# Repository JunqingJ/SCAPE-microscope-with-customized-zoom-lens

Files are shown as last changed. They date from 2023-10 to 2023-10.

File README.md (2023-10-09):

# SCAPE-microscope-with-customized-zoom-lens
Detailed guideline containing both hardware and software to reproduce the SCAPE microscope with home-built zoom lens. Compare with other variations of OPM systems, SCAPE utilizes a galvo mirror for 3D imaging, making the acquisition much faster and drifting-free. Combining it with a home-built zoom lens, the new systems further extends the imaging capabilities to "any immersion medium" which no longer been constrained by the primary objective lens chosen. Such feature opens up much wider potential applications of SCAPE microscope and making the imaging of tissue-
cleared samples possible. 

The overall diagram of the microscope is shown below:



This project intends to offer those very beginner who barely had any optics background a not-so-intimidating starting point. Contents in this repository are mostly practical/hands-on oriented and keywords of theoretical concepts are provided.

Contact: chris.moraes@mcgill.ca or junqing.jiang@mail.mcgill.ca

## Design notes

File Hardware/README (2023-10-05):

List of drivers need to be downloaded:
* In case listed drivers are no longer available from the supplier, please contact chris.moraes@mcgill.ca for a copy
** Drivers that needs to be purchased separately are not included here (AndorSDK3, AndorSDK3 for MATLAB, Bitflow SDK 6.40)

-Laser: CoboltMonitor-6.1.0.0 (https://hubner-photonics.com/downloads/)

-Zoom lens linear stage: Kinesis 1.14.41 (https://www.thorlabs.com/software_pages/ViewSoftwarePage.cfm?Code=Motion_Control&viewtab=0)

-Bright field camera: ThorCam 	3.7.0 (https://www.thorlabs.com/software_pages/viewsoftwarepage.cfm?code=ThorCam)

-Sample stage: USB 4d stage 2.4 (https://picardindustries.com/other/software-downloads/)

-NI DAQ 6009 for galvo mirror: DAQmx

Steps to setup Andor Zyla 4.2+ in MicroManager (V2.0.0):

-Make sure BitFlow and properly installed 

-Open a new configuration and select Devices/Hardware Configuration Wizard/Create new configuration 

-Change the listing into ‘List by Type’, then go to camera/AndorSDK3: SDK3 Device Adaptor for sCMOS camera 

-Click OK, click next, leave everything by default. Don't forget to save the configuration

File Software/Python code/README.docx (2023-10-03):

Python version: 3.8.8 (Anaconda)

Complier: Spyder

Library & Dependency: No extra dependencies need to be downloaded. But make sure both “thorlabs_DDS050.py” and “thorlabs_DDS100.py” are in the same pathway as your main code

Extra: go to Device Manager, find Thorlabs 'APT USB device' (under USB controllers) and on the 'advanced' tab select the 'load VCP' check box to enable COM port

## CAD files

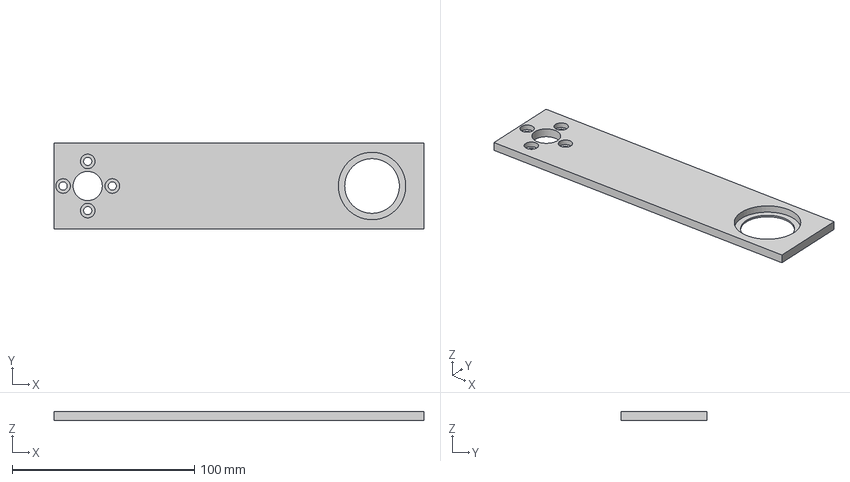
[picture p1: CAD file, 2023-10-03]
Hardware/Machined items/Picard sample arm.stp
203.0 x 47.0 x 5.00 mm

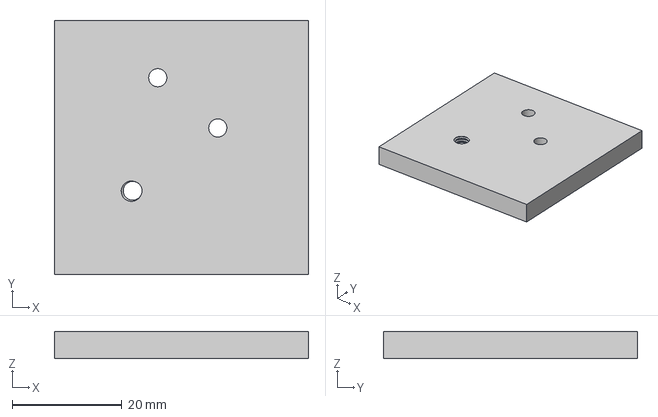
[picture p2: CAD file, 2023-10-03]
Hardware/Machined items/galvo center adaptor.stp
46.2 x 46.2 x 5.00 mm

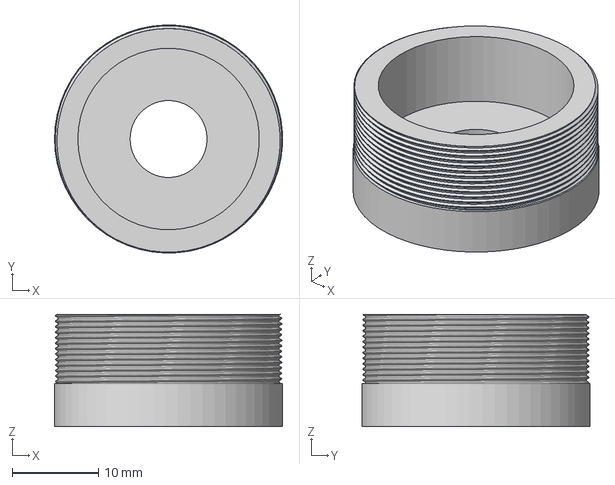
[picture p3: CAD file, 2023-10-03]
Hardware/Machined items/Powell lens.stp
26.4 x 26.4 x 13.0 mm

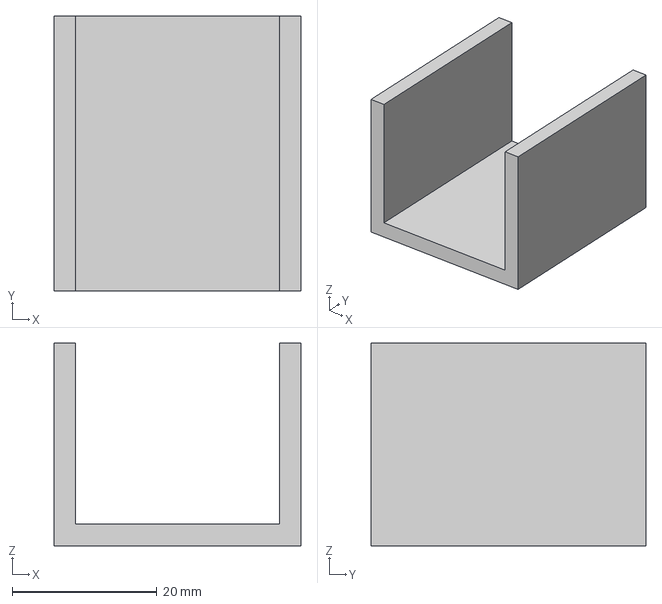
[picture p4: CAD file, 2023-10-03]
Hardware/Machined items/zoom lens spacer2.stp
34.1 x 38.0 x 28.0 mm

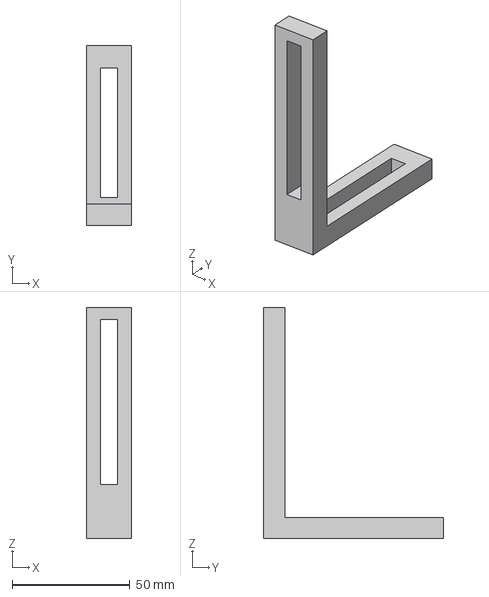
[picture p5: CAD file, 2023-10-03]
Hardware/Machined items/zoom lens angled bracket.stp
19.0 x 76.2 x 97.9 mm

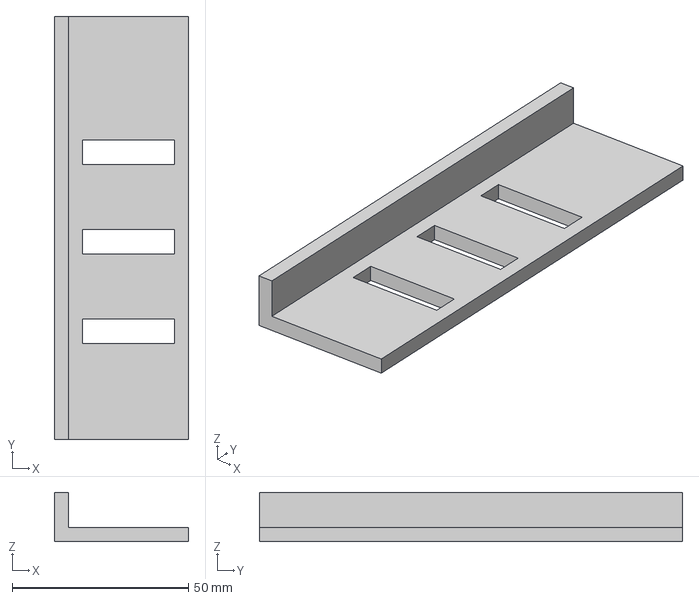
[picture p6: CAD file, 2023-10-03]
Hardware/Machined items/zoom lens guiding rail.stp
38.0 x 120.0 x 14.0 mm

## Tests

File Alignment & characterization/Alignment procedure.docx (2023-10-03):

Part I: Setting up the reference

1. Use a ruler to check the height of excitation laser beam
2. Setup a collimated low power green reference laser at one end of the optical table using Polaris mount. Make sure the center of the beam matches the height of excitation laser
3. Using at least 2 Iris along the beam path to make sure it is parallel in all 3 axes
4. Setup the manual rail at the desired position, leave 3 stages on it. Mount an Iris on the middle stage
5. Position the middle stage so it’s located at the center of reference laser. Replace the Iris with turning mirror and position it until it’s perfect 90 degree
6. Mount the galvo mirror at the end of manual rail. Position the height and rotation angle so the laser hits its center, and the angle is at perfect 90 degree
7. Confirm the height of reference beam at far away position
8. Setup O1 and O2 with their respective tube lens using cage system (see video on how to setup O1 with its cage system so it can be swapped in and out)
9. Input a secondary reference laser from the front end of objective lens. Adjust the position of tube lens until the output beam is collimated. These 2 cage systems can be set aside for later usage

Part II: Fluorescent light pathway until zoom lens

1. Setup the 70mm lens onto the 3rd stage on the rail and position it until laser remains on its reference pathway
2. Adjust the position of the stage until the laser is focused onto the galvo mirror. May need protection eyeglass for more accurate inspection
3. Setup a 50mm lens (or shorter focal distance) before the turning-mirror using a small cage system. Make sure the lens is mounted within a lens tube so it can be screwed in/out easily
4. Adjust the position of the lens so the laser remians on its reference pathway
5. Adjust the position of 50mm lens within the cage until the output laser after galvo is collimated. Then unscrew the lens tube
6. Setup the 88.9mm lens after galvo using a small cage system, adjust the position until the laser remains on its reference pathway
7. Adjust the position of 88.9mm lens within the cage until the output laser is collimated

Part III: Zoom lens: (find details in https://amsikking.github.io/any_immersion_remote_refocus_microscopy/appendix.html#zoom_lens)

Note: May need to machine several right-angle brackets that matches the desired height, guiding rail (check the video) as well as spacers

1. Setup all 3 P, N, P lens and position each linear stage on the plate at its desired position
2. Mount the plate onto the main optical table 2 holes after the 88.9mm lens
3. Place an Iris in between the plate and 88.9mm lens and another Iris far away along the reference laser pathway
4. Run the python code to set the stage at “132.5mm” position
5. Setup the first positive lens group on stage 1, adjust until the laser beam passes the center of faraway Iris (2 axes plus 2 rotation).
6. Close the Iris at the back to its minimum and make sure the back reflection hits the center of Iris in the back. Be gentle when fixing the position as over tightening may affect the alignment
7. Setup the negative lens group on stage 2 following the procedure in step 5 and 6. The 50mm lens may need to be swapped in/out to maintain desired laser spot size at faraway position
8. Setup the second positive lens group on stage 3 following the procedure in step 5 and 6. Make sure the back reflection light is clean and centered at the back Iris
9. Gently loosen the negative lens tube, use the spacer to find the appropriate position with respect to positive lens on stage 3. While fixing the position of negative lens tube, the spacer should be lightly held by the 2 lens tubes. Falling may indicate the imperfect alignment
10. Gently loosen the positive lens tube on stage 1 and follow the procedure in step 9 to find its appropriate position
11. Set up the guiding rail by placing them tightly against the side of the plate. Swap in the 50mm lens
12. Unscrew the plate and move it along the guiding rail until the output beam is collimated. Remove the 50mm lens
13. Setup a diffuser lens (can be made by scratching glass slide using sandpaper) and a small black screen
14. Position the diffuser lens at the focal point of the zoom lens, run the python code that position the zoom lens within its designed range. The speckle pattern observed on black screen can be used as a qualitative check for alignment
15. Remove the diffuser lens and black screen

Part IV: Fluorescent light pathway until O2:

Note: depending on the choice of dichroic mirror and O2, relay lens pair may not be necessary. The exact focal distance of relay lens pair does not particularly matter as long as they produce 1:1 magnification

1. Setup the dichroic mirror right after the zoom lens and position it until the mirror produces a perfect 90 degree reflection
2. Set up another manual rail and put in the 60mm lens. Follow step 4 and 5 in Part II to align the 60mm lens
3. Swap in the 50mm lens and unscrew the O2 from its small cage system
4. Align the second 60mm lens in a cage system following step 4 and 5 in Part II
5. Screw back in the O2 and remove 50mm lens. Fine adjust the alignment of the small cage system

Part V: Tilted alignment between O2 & O3

Note: Following steps involves compromise due to limited working space, ideally the position of O2 is never moved once been fixed in Part IV

1. Use 2 holdfast to mark the position of the stage where O2 is mounted. Then move the stage backwards until enough space is created so that O2 & O3 can be placed face-to-face at 180 degrees
2. Mount O3 with a turning mirror and position it onto a manual z-stage. The entire setup is mounted altogether onto a separate small plate for easier maneuver
3. Place a cage compatible Iris after O3 and place O3 in front of O2
4. Roughly adjust its position until the light spot passes through the center of Iris
5. Fine adjust and fix the height using z-stage and leave all other axes roughly aligned. Move the O2 back to its marked position
6. Start tilting the O3 incrementally, move the plate around after each tilt until the laser spot passes through the center of Iris
7. Depending on the O2 & O3 used, a tilting angle between 40-50 degrees should be aimed. Circular laser spot will start to be clipped into an eclipse/olive as the tilting angle increases
8. After the desired angle is reached (by eyeball, no need to be precise), fine adjust the position of the plate until the output beam is collimated and centered at the Iris
9. Gently fix the position of the plate using holdfast and insert emission filter and another turning mirror to turn the beam upwards
10. Mount camera with the commercial zoom lens and mount them altogether vertically onto a large z-translation stage (see in video)
11. Position the large z-stage until the laser beam roughly hits the center of commercial zoom lens

Part VI: O1 and bright-field imaging system

1. Change the angle of removable turning mirror in Part I so the laser is pointed towards the direction where O1 should be (the turning mirror is set up using separable cube so the base will ensure the angle is fixed once the mirror is inserted)
2. Place the cage system containing O1 onto the stage and mount a cage compatible Iris
3. Position the cage system until the laser spot passes through the center of the Iris
4. Remove O1 from the cage system and insert a secondary reference laser
5. Remove turning mirror and leave that cube empty. Swap in a dichroic mirror that will reflect the reference laser
6. Use a shear plate to check the collimation of beam reflected from the dichroic, adjust the position of O1 cage system until the beam is collimated
7. Bring back the turning mirror and make sure the laser is directed to the bright-field setup
8. Replace 50mm lens with a 100mm lens and adjust its position following step 4 and 5 in Part II
9. Mount the bright-field camera with its camera lens using a cage system and place a cage compatible Iris in front
10. Adjust the position of camera until the laser passes through the center of the Iris. There is no need to maintain 2f condition between the 100mm lens and camera lens, as this will not affect the performance of bright-field imaging system
11. Remove the Iris and secondary reference laser. Swap back O1

Part VII: Light-sheet formation and conditioning

1. Mount Powell lens and cylindrical lenses into rotatable cage plate. Powell lens may need a customized adapter depending on its shape
2. Mount Powell lens and the 50mm cylindrical lens using a cage system, then remove the cage plate containing 50mm cylindrical lens
3. Turn on the excitation laser and set at a low power (~ 3mW) and adjust the height of Powell lens so a vertical light sheet with uniform intensity distribution is formed. The vertical light sheet should be checked using a slit
4. Place the cage plate containing the 50mm cylindrical lens back into the cage system as well as a slit. Adjust the rotational angle of 50mm cylindrical lens until a perfect vertical light sheet is formed
5. Adjust the position of the 50mm cylindrical lens until a collimated light sheet is formed. If a collimated light sheet cannot be formed, it indicates the angle of cylindrical lens is 90 degrees off
6. Place the cage system in front of the excitation laser and using both reflected light and slit to confirm it’s placed at the center of the laser pathway
7. Set up the 75mm cylindrical lens and turning mirror onto a 2-axis manual stage (see in video) and using cage system to ensure it is positioned at 90 degrees
8. Place the 2-axis manual stage so it roughly aims at the center of dichroic mirror
9. Adjust the rotational angle until a beam converging on y-axis is formed (collimated on x-axis)
10. Adjust the y-axis knob on the manual stage until the output light sheet from 75mm cylindrical lens passes through the center of slit
11. Adjust the x-axis knob on the manual stage until the light sheet passes through the center of each following spherical lens. This doesn’t need to be precise
12. Prepare a glass of fluorescein solution and immerse the tip of O1 to visualize the light sheet
13. Looking from the size of the objective lens, check if the light sheet is emitted from the center of the tip
14. If not, carefully adjust the height of the cage system mounted on the s-axis manual stage until the light sheet is emitted from the center of the tip
15. Lossen the 75mm lens and adjust its position until the light sheet forms a focused spot onto the center of the galvo mirror
16. Remove the glass of fluorescein solution and clean the tip of O1

Part VIII: Tilt angle fine turning and quality check

1. Prepare droplets of 1% agarose gel containing 200nm fluorescent beads following the protocol
2. Place the sample under O1 and open MicroManager for live viewing
3. Set laser power at 20 mW (488nm) and adjust the intensity upper limit on MicroManager to around 500
4. Adjust the height of sample using the 4D stage and a focused thin line with PSF should be observed
5. If no PSF can be observed at all no matter what, it indicates the poor alignment during previous steps
6. Adjust the x-axis knob on the manual stage setup in Part VII (make sure toward the right direction as a reversely tilted light sheet won’t do anything) and the sharp region should start to grow as the tilt angle increases
7. Adjust the knob until the optimal angle is found that matches the tilting angle between O2 & O3. It is likely not the entire aperture will be sharp
8. If the PSF is blurry, it is usually caused by defocusing. Attempts can be made by adjusting the focusing ring on the commercial zoom lens but not suggested. Ideally, re-alignment between O2 & O3 should be performed until sharp PSF can be observed without adjusting the commercial zoom lens

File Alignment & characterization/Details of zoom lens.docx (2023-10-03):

- The most detailed explanation of the design of zoom lens can be found at https://github.com/amsikking/any_immersion_remote_refocus_microscopy. This document does not include any theories behind the design and modelling of a zoom lens as it is far too complicated and way beyond my current knowledge.
- Component list

Optical Part | Part description | Part number (Vendor) | Number
Positive group 1 | 300mm aspherical lens | 47649 (Edmund Optics) | 2
Negative group | N 150mm lens | 62495 (Edmund Optics) | 1
Positive group 2 | 250mm aspherica lens | 47647 (Edmund Optics) | 2
Mounting | Part description | Part number (Vendor)
Linear stage | | DDS050 (Thorlabs) | 2
Linear stage | | DDS100 (Thorlabs) | 2
Post | 1'' | RS1 (Thorlabs) | 2
Slip ring | | SM1RC (Thorlabs) | 3
Mounting plate | | UPB2 (Thorlabs) | 3
Spacer ring | | SM1S1M (Thorlabs) | 2

- Calculation of desired focal length
  - The magnification of a pair of lenses with light enters from lens one can be described as (FL_2)/(FL_1)
  - To avoid spherical aberration at remote refocusing point, the magnification between O1 and O2 needs to be the same as refractive index of the immersion medium
  - Using this microscope setup and water as immersion medium as example:

M_(O1) ×(F_(TL1))/(F_(O1))×(F_(SL2))/(F_(SL1))×(F_(O2))/(F_(ZL))×1/(M_(O2))

=20×150/180×88.9/75×200/f×1/20=1.33

f=148.54

  - The focal length of an objective lens is an intrinsic value and often not reported by the manufacturer. A list for focal length for objective lens from major manufacturers can be found in https://amsikking.github.io/microscope_objectives/tube_lens.html
- Plossl lens:

The shorter focal length of a lens, the greater curvature would be and leads to worse imaging quality. However, it is possible to construct a Plossl lens pair to partially avoid this issue. Essentially Plossl lens is formed using 2 identical aspherical lenses by placing them close to each other and the resulting focal length of the lens pair will be halved compared to individual lenses. In this zoom lens, both positive lens group are constructed this way with spacer ringer separating 2 identical lenses.

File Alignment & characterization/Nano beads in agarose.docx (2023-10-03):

This protocol is adapted from Alfred (https://github.com/amsikking/fluorescent_beads_in_agarose) and water dipping objective lens is assumed. Be sure to differentiate between water dipping and water immersion objective lens before using this protocol.

Fluorescent nanobeads in agarose:

Reagent:

- 0.2um TetraSpeck nanosphere
- Ultra-pure agarose powder
- RO water
- 35mm petri dish

Steps:

1. Weight 0.1g (can be adjusted and no need to be precise) of agarose powder in a test tube
2. Add in RO water to reach 1% w/v ratio
3. Cap the test tube using rubber septum and microwave the test tube at 5s interval for 40s or until the powder is completely dissolved
4. Prepare an Eppendorf and preset the volume on pipette tips (396ul, 4ul and 50ul), bring the vortex and petri dish to benchtop. Make everything ready to use as following steps should be performed as fast as possible
5. When the agarose solution reaches the temperature slightly hot for hand, extract 396ul of the solution into the Eppendorf
6. Add in 4ul of nano beads and vortex for 10s
7. Extract 50ul of the mixture and drop it onto the petri dish. 50ul will be enough to form multiple droplets and the size of each droplet does not matter
8. Wait until the agarose solution fully gels and add in enough RO water to immerse the gel droplets

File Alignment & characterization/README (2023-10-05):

-This folder contains step by step guideline for alignment of the entire system including parts that are used 

-For machined parts, step files can be found in hardware folder

-Videos of alignment procedure is coming "soon"

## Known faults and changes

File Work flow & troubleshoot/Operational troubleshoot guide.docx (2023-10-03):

Zoom lens problem identification:

- Zoom lens is the part that most likely to get in trouble during usage
- If any of 3 stages cannot be connected in Kinesis even after manual connection, go to turn off cubes
- If cubes turned off properly, then turn on the cube after about 10s and try Kinesis again. Problems should be resolved. Following next section to set the “closed position”
- If cubes do not turn off, then turn off the controller hub. Cubes will be forced off, wait for 10s and turn on the controller hub and then turn on individual cubes. Try Kinesis again to see if communication can be established properly. If yes, then following next section to set the “closed position”
- If communication of any cube cannot be established properly after restarting the controller hub, then turn off cubes and controller hub, reboot the computer. Then turn back on controller hub and cubes. Then follow the next section to set the “closed position”
- Whenever turning on a cube, make sure to wait until its starting-up procedure is completed. “Completed” or “disabled” message indicate proper restart. “Phase error” indicates starting-up failed, it usually caused by the linear stage too close to the upper/lower limit. Gently move the stage a bit towards middle point and restart the cube again.

Manually setting zoom lens to “closed position”:

- The “closed position” is carefully selected to prevent crash of stages during movement
- Open Kinesis
- Enable one fo the 50 mm stages; Test to see if it holds position, to figure out which unit is being enabled.
- Zoom stages do not coordinate with Kinesis order; 50 mm stages are lens 1 and 3 (labelled DD050 on the screen).
- ON ZOOM LENS 1, (50mm stage): set to home. then set to 50
- Enable Zoom lens 2 (100 mm stage): set to home; move to 70
- On Zoom Lens 3 (50 mm stage): set to home, set to 0
- On Zoom Lens 2 (100 mm stage AGAIN): set back to 0 (this procedure avoids crashes)
- On Zoom lens 1: set this to 20
- SO FINAL POSITION: lens 1: 20mm; Lens 2: 0mm; Lens 3: 0mm – this is the CLOSE POSITION.
- Close Kinesis

Thorcam troubleshoot:

- Occasionally, Thorcam software will freeze and not respond
- Try close the software in Task Manager and reopen the software, problem is usually resolved
- If not, reboot the computer and the problem will be resolved

Abnormal laser power:

- Currently, all lasers are set at constant power mode without any complex modulation
- Occasionally, the laser power will jump to 1mW and stay there
- Turn off the laser, set the power to the desired value and turn the laser back on. Problem is usually resolved

Laser COM port cannot be connected:

- This is most likely caused by double opening the control software. Make sure you are not opening the software again while it was running already
- If this is not caused by the double opening, then unplug the signal wire and reconnect
- If reconnecting the signal wire does not resolve the problem, unplug power supply for laser. Make sure all laser has been turned off before unplugging. Reconnect the power and the problem should be resolved

Camera communication cannot be established:

- Check if camera is turned on
- Check if there is another software occupying the communication port (MicroManager, Matlab or Python)
- It is also possible that the camera was not closed properly in software last time (only happens when writing code and debugging). In this case, go to Matlab and run the following code
- When writing and testing the code, it is common that the camera is opened properly, and your code fails before it’s been closed. Be sure to close the camera in command window before proceeding to debug

addpath('C:\Program Files\MATLAB\R2021a\toolbox\AndorSDK3')

[rc] = AT_InitialiseLibrary();

AT_CheckError(rc);

[rc] = AT_Command(hndl,'AcquisitionStop');

AT_CheckWarning(rc);

[rc] = AT_Flush(hndl);

AT_CheckWarning(rc);

[rc] = AT_Close(hndl);

AT_CheckWarning(rc);

[rc] = AT_FinaliseLibrary();

AT_CheckWarning(rc);

disp('Camera shutdown');

Severly clipped image:

- It is most likely caused by Iris not been fully opened. Check all Iris in the light pathway to make sure all of them are opened entirely

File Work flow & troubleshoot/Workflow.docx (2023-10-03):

On the computer – there’s no order how to open this.

- Open Kinesis (Thorlab’s software for linear stage)
  - check if all 3 stages are connected properly. If yes, then close the software and proceed to next step.
  - If not, click connect and manually select all stages that are not connect and try connecting. If successful, then close the software and proceed.
  - If any stage cannot be connected after manual connection, follow instruction in Troubleshoot. (If linear stage can be opened properly in Kinesis, it should be controlled properly in Python as well)
- Open Spyder (Python)
  - have to run the program in its entirey first, to import the modules. and then close the zoom lens after that.
  - WE ARE IMAGING In WATER, so focal length (config_f_mm) should be set to 148.54. Focal length=197.556/RI
  - Go into Spyder, change this in the code for zoom_lens.py; and line ~150ish
- Open ThorCam – for the brightfield
- Open USB 4D stage
  - click on “Go To Reference” to position the stage in the midpoint of the field
- Open Matlab
  - Go to “Set_voltage” script and run it
- Open Micromanager.
  - Hardware config is camera.cfg. Click Okay. If you see an error, it’s because camera is not on, and needs to be turned on.
- Open Cobolt Monitor for the laser.

Starting the microscope

- Make sure the brightfield mirror is in
- In Spyder, go to zoomlens.py, and run
- Prep sample by adding water
- Manually raise the labjack to dip the objective.
  - Make sure there is no bubble trapped with the dipping objective. If so, raise, wipe with lens paper; lower again.
- Turn LED brightfield ON
- Go to ThorCam. Select the only available camera. Click Run.
- Use Picard stage software to move.
  - Its Z, Y and Z axis is different from the conventional definition. Y corresponding to up/down
- Change the default exposure on the Zyla camera. Then Click “Live” in MicroManager
  - To do this, go to Micromanager. Devices > Device Property Browser > Andor sCMOS Camera Exposure…. Change to 75ms for example. . This should look a little funky; in that it’ll be focused on only one parts.

3D image acquisition

- Turn on the laser using Cobolt software
- Open the shutter.
  - Won’t see 375nm (outside of visible)
- Make sure MicroManager is closed before using MATLAB for 3D acquisition
- Following comments in MATLAB code to enter the proper parameters
  - Use Filenames with an Underscore at the end so that the numbering happens automatically.

Shutdown Procedure

- IN MATLAB command line type in: write(dq,0)
  - This is to set the galvo corresponding to zero, in case of power shut down. This is just to be cautious, so that when power comes back, it doesn’t see a very large signal.
- Close Matlab
- In Spyder, run: zoom_lens.close()
  - To make sure the zoom lens does not collide.
- Close Spyder
- Close ThorCam
- Lower labjack to the lowest point
- Remove sample
- Wipe O1 with washing solution or 70% ethanol on the lens paper. Swab gently.
- Put turning mirror back in.
- Turn off the camera
- Picard stage – set to Home for X, Y, Z. Shut down.

# Troubleshoot

Thorlabs software to operate this is Kinesis

Enable one fo the 50 mm stages; Test to see if it holds position, to figure out which unit is being enabled.

Zoom stages do not coordinate with Kinesis order; 50 mm stages are lens 1 and 3 (labelled DD050 on the screen).

ON ZOOM LENS 1, (): set to home. then set to 50

Enable Zoom lens 2 (100 mm stage): set to home; move to 70

On Zoom Lens 3 (50 mm stage): set to home, set to 0

On Zoom Lens 2 (100 mm stage AGAIN): set back to 0 (this procedure avoids crashes)

On Zoom lens 1: set this to 20

SO FINAL POSITION: lens 1: 20mm; Lens 2: 0mm; Lens 3: 0mm – this is the CLOSE POSITION.

Close Kinesis

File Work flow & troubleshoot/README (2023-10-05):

-The workflow of this microscope is absolutely not optimized as it is mainly based on commercial software from individual hardware supplier

-The sole reason why MicroManager was not used for integrated control is because it lacks ability to send out fast analogue signal required by galvo mirror

-MicroManager plugin for analogue signal exists but was designed for OpenSIM and can be tricky to adapt into this system

-It is highly suggested to explore the option of integrated control through PycroManager (which can also be benefited from using napari)

-Alternatively, pure home written integrated control code (and GUI) can be considered. see reference at Alfred's SOLS microscope (https://github.com/amsikking/SOLS_microscope)

-For image post-processing, no completed workflow has been established yet. But one can refer to Alfred's post-processing code for SOLS microscope (https://github.com/amsikking/SOLS_microscope_data_processing) as a starting point
